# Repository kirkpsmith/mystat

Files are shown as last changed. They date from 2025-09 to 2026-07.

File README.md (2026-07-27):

# mystat

A USB-controlled potentiostat/galvanostat for electrochemistry measurements.

## Introduction
This repository contains all the necessary design files to build a USB-controlled potentiostat/galvanostat.  This repository is a modification of the original [tdstatv3](https://github.com/thomasdob/tdstatv3) designed by Thomas Dobbelaere and described in detail at https://arxiv.org/pdf/1701.07650.pdf.  The purpose of this fork is to make design changes that facilitate placing the instrument inside a protected enclosure suitable for an electrochemical research environment, including a wet chemical lab bench, fume hood, or glove box.

This version of the hardware design uses a PCB with dimensions of 55.5 mm by 70 mm to fit an EMI-shielded [extruded aluminum case](https://www.hammfg.com/files/parts/pdf/1457C801E.pdf) (IP 54 rated).  This board will also fit a similar watertight [extruded aluminum case](https://www.hammfg.com/files/parts/pdf/1457C801.pdf) (IP 65 rated).  The terminal block and surface mounted USB mini-B connector in the original tdstav3 design by Thomas Dobbelaere were replaced with IP 67 rated circular connectors for the USB and electrode cables.

In order to fit the case, tall components (such as the reed relays and crystal) had to be moved from the board edges that slide into the slots in the extruded aluminum.  As a result, the entire PCB layout was changed.  All traces were made as wide as possible given the PCB size constraints and component footprints.  In addition, this forked design eliminates the power and mode LEDs present in the original tdstatv3.  The choice to eliminate LEDs was made to avoid the need for creating holes in the case that would accommodate them.

## USB access on Linux
In order to access the device without requiring root privileges, create a file
`/etc/udev/rules.d/99-tdstatv3.rules` containing the line

```
SUBSYSTEM=="usb", ATTRS{idVendor}=="a0a0", ATTRS{idProduct}=="0002", GROUP="plugdev", MODE="0666"
```

If you are using an Arduino or similar to control pumps for flow battery experiments, you will need to make a similar file for that device, for example
`/etc/udev/rules.d/99-arduino.rules` and
```
SUBSYSTEM=="usb", ATTR{idVendor}=="1a86", ATTR{idProduct}=="7523", GROUP="plugdev", MODE="0666"
```

This assumes that the current user is a member of the `plugdev` group, and that the default USB Vendor and Product ID's
as coded in the microcontroller firmware are used; if not, these values need to be adjusted.

Reload of rules may be needed:
```
sudo udevadm control --reload
sudo udevadm trigger
```

## Windows Driver

To install the USB drivers in Windows, you must have Windows version 7 or later.  Download and run the program Zadig.exe found [here](https://github.com/pbatard/libwdi/releases/download/v1.5.1/zadig-2.9.exe).  The potentiostat should appear in the device list as "USB potentiostat/galvanostat".  Install the driver named "libusbK".

More information on Zadig can be found from its authors at: https://zadig.akeo.ie/

Zadig is based on libwdi and is licensed under GPLv3. The Zadig source code is found in the examples directory of the libwdi archive. The latest version of the source code may be downloaded from the git repository: https://github.com/pbatard/libwdi

## Credits
tdstatv3 created by:

* Thomas Dobbelaere
* email: thomas.dobbelaere@gmail.com

Previous fork created by:

* Matthew Yates
* email: myates@che.rochester.edu

Current fork created by:

* [Daniel Fernandez Pinto](https://chemisting.com) and [Kirk Smith](https://dualpower.supply)

## License
The contents of this repository are licensed under the GNU General Public License (GPL).

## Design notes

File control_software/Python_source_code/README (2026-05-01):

In this directory, create a virtual environment, activate it, and install the required packages:
```
python3 -m venv .venv
source .venv/bin/activate
python3 -m pip install -r requirements.txt
```

Run the program (sudo may be needed on Linux for USB privileges)
```
sudo .venv/bin/python mystat.py
```

On Linux, the following commands are sometimes needed:
```
export LD_LIBRARY_PATH=$(python3 -c "import PyQt5.QtCore; print(PyQt5.QtCore.QLibraryInfo.location(PyQt5.QtCore.QLibraryInfo.LibrariesPath))"):$LD_LIBRARY_PATH
export QT_QPA_PLATFORM_PLUGIN_PATH=$(python3 -c "import PyQt5.QtCore; print(PyQt5.QtCore.QLibraryInfo.location(PyQt5.QtCore.QLibraryInfo.PluginsPath))")

```

To package the app, download [appimagetool](https://github.com/AppImage/appimagetool/releases) to this directory, rename to `appimagetool`, and run
```
./build-appimage.sh
 ```

To update requirements.txt:

```
python -m pip freeze > requirements.txt
```

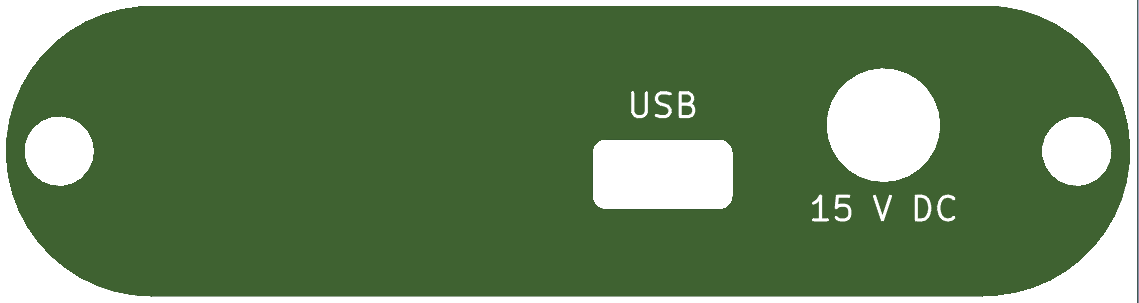
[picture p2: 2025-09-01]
hardware/backpanel/backpanel_image.png

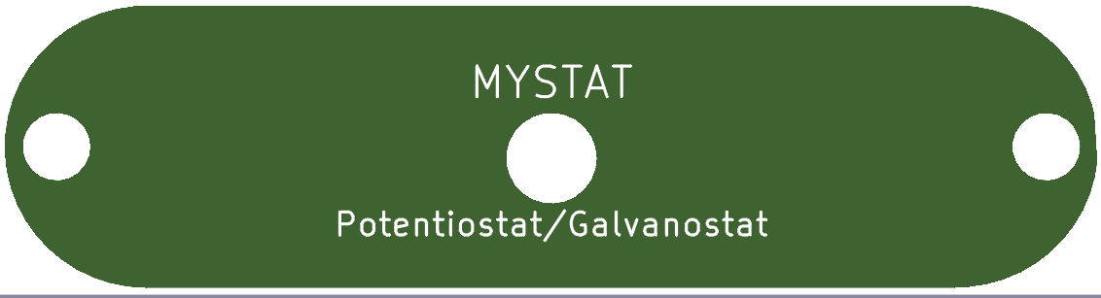
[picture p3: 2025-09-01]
hardware/frontpanel/frontpanel_image.png

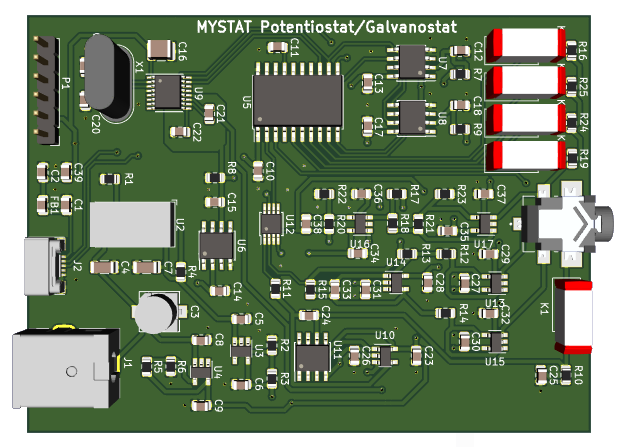
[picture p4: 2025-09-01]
hardware/mystat_circuit_board/circuit_board_image.png

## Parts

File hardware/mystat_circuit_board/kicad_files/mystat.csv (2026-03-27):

Value | Reference | Footprint | Qty | Part Number
10 nF | C1,C22 | Capacitor_SMD:C_0805_2012Metric | 2 | C0805C103J5GACTU
100 nF | C2,C10,C11,C12,C13,C14,C15,C17,C18,C23,C25,C26,C27,C28,C29,C30,C31,C32,C34,C35,C36,C37 | Capacitor_SMD:C_0805_2012Metric | 22 | 08055C104KAT2A
47 uF | C3 | my_footprints:EEE-FT1V470AR | 1 | EEE-FT1V470AR
4.7 uF | C4,C7 | Capacitor_SMD:C_1206_3216Metric | 2 | CL31B475KBHNNNE
4.7 uF | C5,C6,C8,C9,C39 | Capacitor_SMD:C_0805_2012Metric | 5 | C2012X7R1V475K125AC
10 uF | C16 | Capacitor_SMD:C_1210_3225Metric | 1 | CL32B106KBJNNWE
12 pF | C19,C20,C33,C38 | Capacitor_SMD:C_0805_2012Metric | 4 | CC0805JRNPO9BN120
3.3 nF | C21 | Capacitor_SMD:C_0805_2012Metric | 1 | GRM2165C1H332JA01D
4700 pF | C24 | Capacitor_SMD:C_0805_2012Metric | 1 | CC0805KRX7R9BB472
ILBB0805ER320V | FB1 | Capacitor_SMD:C_0805_2012Metric | 1 | ILBB0805ER320V
PJ-063AH | J1 | my_footprints:CUI_PJ-063AH | 1 | PJ-063AH
2173157-3 | J2 | my_footprints:CONN_2173157-3 | 1 | 2173157-3
SJ1-42534-SMT | J3 | my_footprints:CUI_SJ1-42534-SMT | 1 | SJ1-42534-SMT-TR
9011-05-11 | K1,K2,K3,K4,K5 | my_footprints:relay_9011-05-11 | 5 | 9011-05-11
ICSP | P1 | Connector_PinHeader_2.54mm:PinHeader_1x06_P2.54mm_Vertical | 1 | PRPC006SAAN-RC
60.4 kΩ | R1 | Resistor_SMD:R_0805_2012Metric | 1 | ERJ-6ENF6042V
8.87 kΩ* | R2 | Resistor_SMD:R_0805_2012Metric | 1 | ERA-6AEB8871V
88.7 kΩ* | R3 | Resistor_SMD:R_0805_2012Metric | 1 | ERJ-PB6B8872V
178 kΩ | R4 | Resistor_SMD:R_0805_2012Metric | 1 | ERJ-6ENF1783V
294 kΩ* | R5 | Resistor_SMD:R_0805_2012Metric | 1 | ERJ-PB6B2943V
174 kΩ* | R6 | Resistor_SMD:R_0805_2012Metric | 1 | ERJ-PB6B1743V
1k | R7,R9 | Resistor_SMD:R_0805_2012Metric | 2 | RC0805FR-071KL
10k | R8,R11 | Resistor_SMD:R_0805_2012Metric | 2 | RC0805FR-0710KL
27R | R10 | Resistor_SMD:R_0805_2012Metric | 1 | ERJ-6ENF27R0V
402k* | R12,R14 | Resistor_SMD:R_0805_2012Metric | 2 | ERA-6AEB4023V
75k* | R13,R15,R17,R18,R20,R22 | Resistor_SMD:R_0805_2012Metric | 6 | ERA-6AEB753V
100k* | R16 | Resistor_SMD:R_0805_2012Metric | 1 | ERA-6AEB104V
1k* | R19 | Resistor_SMD:R_0805_2012Metric | 1 | ERA-6AEB102V
18k* | R21 | Resistor_SMD:R_0805_2012Metric | 1 | ERA-6AEB183V
2k* | R23 | Resistor_SMD:R_0805_2012Metric | 1 | ERA-6AEB202V
10R* | R24 | Resistor_SMD:R_0805_2012Metric | 1 | 2-1625868-7
1R* | R25 | Resistor_SMD:R_0805_2012Metric | 1 | RL1220S-1R0-F
LTM8045 | U2 | my_footprints:BGA-40_6.25x11.25mm_Layout5x8_P1.25mm | 1 | LTM8045IY
ADP7182AUJZ-R7 | U3 | my_footprints:TSOT-23-5 | 1 | ADP7182AUJZ-R7
ADP7118AUJZ-5.0-R7 | U4 | my_footprints:TSOT-23-5 | 1 | ADP7118AUJZ-5.0-R7
PIC16F1459 | U5 | my_footprints:SOIC-20W | 1 | PIC16F1459-I/SO
ADR421 | U6 | my_footprints:SOIC-8 | 1 | ADR421ARZ
MCP3550-60 | U7,U8 | my_footprints:SOIC-8 | 2 | MCP3550-60E/SN
DAC1220 | U9 | my_footprints:DAC1220 | 1 | DAC1220E
OPA192 | U10,U13,U14,U15,U16,U17 | my_footprints:OPA192 | 6 | OPA192IDBVR
BUF634A | U11 | my_footprints:SOIC-8 | 1 | BUF634AIDR
ADG1419 | U12 | my_footprints:MSOP-8_3x3mm_P0.65mm | 1 | ADG1419BRMZ-REEL7
2.5 MHz | X1 | Crystal:Crystal_HC49-U_Vertical | 1 | ECS-25-S-1X

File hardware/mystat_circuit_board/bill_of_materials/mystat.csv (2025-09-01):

References | Manufacturer | Part Number | Value | Footprint | Quantity | Price(each) | Source
C1, C22 | KEMET | C0805C103J5GACTU | 10 nF | C_0805_2012Metric | 2 | 0.76 | Digikey ‎399-7992-1-ND‎
C16 | Samsung Electro-Mechanics | CL32B106KBJNNWE | 10 µF | C_1210_3225Metric | 1 | 0.66 | Digikey ‎1276-3388-1-ND‎
C19, C20, C33, C38 | Yageo | CC0805JRNPO9BN120 | 12 pF | C_0805_2012Metric | 4 | 0.11 | Digikey ‎311-1100-1-ND‎
C2, C10, C11, C12, C13, C14, C15, C17, C18, C23, C25, C26, C27, C28, C29, C30, C31, C32, C34, C35, C36, C37 | AVX Corporation | 08055C104KAT2A | 0.1 µF | C_0805_2012Metric | 22 | 0.15 | Digikey ‎478-1395-1-ND
C21 | Murata Electronics North America | GRM2165C1H332JA01D | 3.3 nF | C_0805_2012Metric | 1 | 0.25 | Digikey ‎490-1632-1-ND‎
C24 | Yageo | CC0805KRX7R9BB472 | 4700 pF | C_0805_2012Metric | 1 | 0.11 | Digikey ‎311-1133-1-ND‎
C3 | Panasonic Electronic Components | EEE-FT1V470AR | 47 μF | EEE-FT1V470AR | 1 | 0.5 | Digikey ‎PCE5014CT-ND‎
C4, C7 | Samsung Electro-Mechanics | CL31B475KBHNNNE | 4.7 μF | C_1206_3216Metric | 2 | 0.36 | Digikey ‎1276-2789-1-ND‎
C5, C6, C8, C9, C39 | TDK Corporation | C2012X7R1V475K125AC | 4.7 µF | C_0805_2012Metric | 5 | 0.73 | Digikey ‎445-7555-1-ND‎
FB1 | Vishay Dale | ILBB0805ER320V | Ferrite_Bead | C_0805_2012Metric | 1 | 0.1 | Digikey 541-2296-1-ND‎
J1 | CUI Inc. | PJ-063AH | PJ-063AH | CUI_PJ-063AH | 1 | 1.36 | ‎Digikey CP-063AH-ND‎
J2 | TE Connectivity AMP Connectors | 2173157-3 | 2173157-3 | CONN_2173157-3 | 1 | 3.39 | Digikey A124356CT-ND‎
J3 | CUI Inc. | SJ1-42534-SMT-TR | SJ1-42534-SMT | CUI_SJ1-42534-SMT | 1 | 1.2 | Digikey CP1-42534SJCT-ND
K1, K2, K3, K4, K5 | Coto Technology | 9011-05-11 | 9011-05-11 | relay_9011-05-11 | 5 | 7.97 | Digikey 306-1131-ND‎
P1 | Sullins Connector Solutions | PRPC006SAAN-RC | ICSP | PinHeader_1x06_P2.54mm_Vertical | 1 | 0.19 | Digikey S1011EC-06-ND‎
R1 | Panasonic Electronic Components | ERJ-6ENF6042V | 60.4 kΩ | R_0805_2012Metric | 1 | 0.1 | Digikey P60.4KCCT-ND‎
R10 | Panasonic Electronic Components | ERJ-6ENF27R0V | 27R | R_0805_2012Metric | 1 | 0.1 | Digikey P27.0CCT-ND‎
R12, R14 | Panasonic Electronic Components | ERA-6AEB4023V | 402k* | R_0805_2012Metric | 2 | 0.36 | Digikey P402KDACT-ND‎
R13, R15, R17, R18, R20, R22 | Panasonic Electronic Components | ERA-6AEB753V | 75k* | R_0805_2012Metric | 6 | 0.36 | Digikey P75KDACT-ND
R16 | Panasonic Electronic Components | ERA-6AEB104V | 100k* | R_0805_2012Metric | 1 | 0.36 | Digikey P100KDACT-ND
R19 | Panasonic Electronic Components | ERA-6AEB102V | 1k* | R_0805_2012Metric | 1 | 0.36 | Digikey P18KDACT-ND
R2 | Panasonic Electronic Components | ERA-6AEB8871V | 8.87 kΩ* | R_0805_2012Metric | 1 | 0.36 | Digikey P8.87KDACT-ND‎
R21 | Panasonic Electronic Components | ERA-6AEB183V | 18k* | R_0805_2012Metric | 1 | 0.36 | Digikey P18KDACT-ND
R23 | Panasonic Electronic Components | ERA-6AEB202V | 2k* | R_0805_2012Metric | 1 | 0.36 | Digikey P2.0KDACT-ND‎
R24 | TE Connectivity Passive Product | 2-1625868-7 | 10R* | R_0805_2012Metric | 1 | 0.53 | Digikey A110351CT-ND
R25 | Susumu | RL1220S-1R0-F | 1R* | R_0805_2012Metric | 1 | 0.33 | Digikey RL12S1.00FCT-ND
R3 | Panasonic Electronic Components | ERJ-PB6B8872V | 88.7 kΩ* | R_0805_2012Metric | 1 | 0.36 | Digikey P20816CT-ND
R4 | Panasonic Electronic Components | ERJ-6ENF1783V | 178 kΩ | R_0805_2012Metric | 1 | 0.1 | Digikey ‎P178KCCT-ND‎
R5 | Panasonic Electronic Components | ERJ-PB6B2943V | 294 kΩ* | R_0805_2012Metric | 1 | 0.36 | Digikey P20873CT-ND‎
R6 | Panasonic Electronic Components | ERJ-PB6B1743V | 174 kΩ* | R_0805_2012Metric | 1 | 0.36 | Digikey P20847CT-ND‎
R7, R9 | Yageo | RC0805FR-071KL | 1k | R_0805_2012Metric | 2 | 0.1 | Digikey 311-1.00KCRCT-ND
R8, R11 | Yageo | RC0805FR-0710KL | 10k | R_0805_2012Metric | 2 | 0.1 | Digikey 311-10.0KCRCT-ND‎
U10, U13, U14, U15, U16, U17 | Texas Instruments | OPA192IDBVR | OPA192 | OPA192 | 6 | 2.68 | Digikey 296-42105-1-ND‎
U11 | Texas Instruments | BUF634AIDR | BUF634A | SOIC-8 | 1 | 2.92 | Digikey 296-53619-1-ND‎
U12 | Analog Devices Inc. | ADG1419BRMZ-REEL7 | ADG1419 | MSOP-8_3x3mm_P0.65mm | 1 | 4.53 | Digikey ADG1419BRMZ-REEL7CT-ND‎
U2 | Linear Technology/Analog Devices | LTM8045IY | LTM8045 | BGA-40_6.25x11.25mm_Layout5x8_P1.25mm | 1 | 21.07 | Digikey LTM8045IY-ND‎
U3 | Analog Devices Inc. | ADP7182AUJZ-R7 | ADP7182AUJZ-R7 | TSOT-23-5 | 1 | 3.71 | Digikey ADP7182AUJZ-R7CT-ND‎
U4 | Analog Devices Inc. | ADP7118AUJZ-5.0-R7 | ADP7118AUJZ-5.0-R7 | TSOT-23-5 | 1 | 2.27 | Digikey ADP7118AUJZ-5.0-R7CT-ND
U5 | Microchip Technology | PIC16F1459-I/SO | PIC16F1459 | SOIC-20W | 1 | 1.77 | Digikey PIC16F1459-I/SO-ND‎
U6 | Analog Devices Inc. | ADR421ARZ | ADR421 | SOIC-8 | 1 | 6.81 | Digikey ‎ADR421ARZ-REEL7CT-ND
U7, U8 | Microchip Technology | MCP3550-60E/SN | MCP3550-60 | SOIC-8 | 2 | 3.98 | Digikey MCP3550-60E/SN-ND‎
U9 | Texas Instruments | DAC1220E | DAC1220 | DAC1220 | 1 | 19.8 | Digikey DAC1220E-ND‎
X1 | ECS Inc. | ECS-25-S-1X | 2.5 MHz | Crystal_HC49-U_Vertical | 1 | 1.13 | Digikey X1003-ND‎
E1 | Tensility International | 10-00340 | N.A. | N.A. | 1 | 4.44 | Digikey ‎839-1035-ND
E2 | Cinch Connectivity Solutions Johnson | 105-0302-001 | N.A. | N.A. | 1 | 1.14 | Digikey J103-ND
E3 | Cinch Connectivity Solutions Johnson | 105-0303-001 | N.A. | N.A. | 1 | 1.28 | Digikey J104-ND
E4 | Cinch Connectivity Solutions Johnson | 105-0304-001 | N.A. | N.A. | 1 | 1.17 | Digikey J301-ND
E5 | Cinch Connectivity Solutions Johnson | 105-0301-001 | N.A. | N.A. | 1 | 1.17 | Digikey J300-ND
E6-E9 | Cal Test Electronics | CT3759-0 | N.A. | N.A. | 4 | 2 | Digikey CT3759-0-ND
E10 | CUI Inc. | SDI30-15-U-P5 | N.A. | N.A. | 1 | 17.88 | Digikey 102-4106-ND
E11 | Hammond Manufacturing | 1455B802 | N.A. | N.A. | 1 | 9.6 | Digikey HM1117-ND
E12 | CUI Devices | AC-C13 NA | N.A. | N.A. | 1 | 3.76 | Digikey T1249-C13-NA-ND

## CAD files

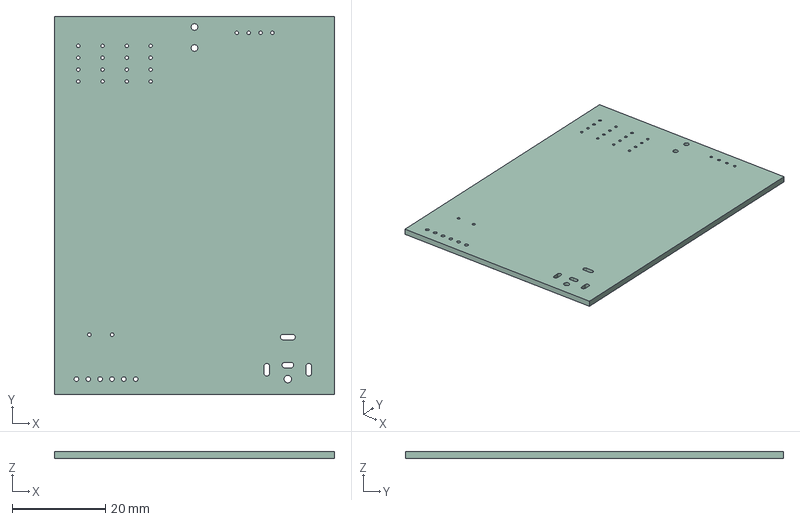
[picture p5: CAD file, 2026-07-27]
hardware/mystat_circuit_board/kicad_files/.step
60.0 x 81.0 x 1.51 mm

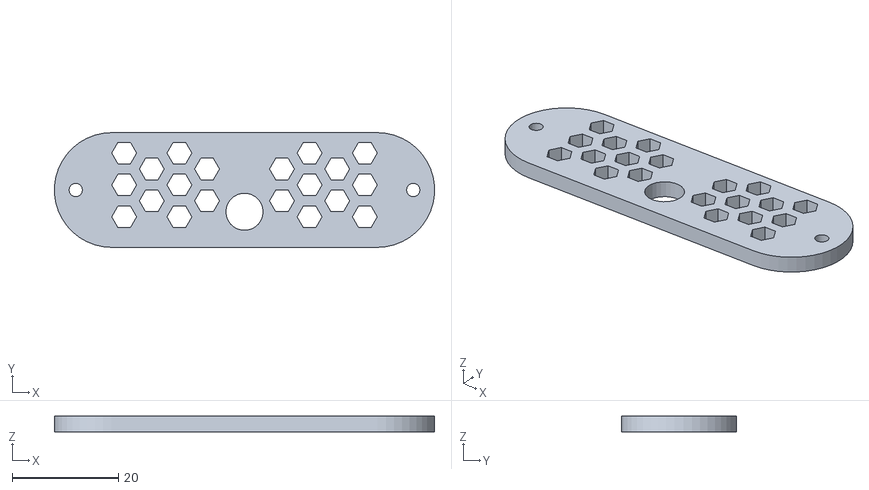
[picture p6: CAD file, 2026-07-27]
hardware/printable_case/Cable Panel.stl
71.5 x 21.6 x 3.00

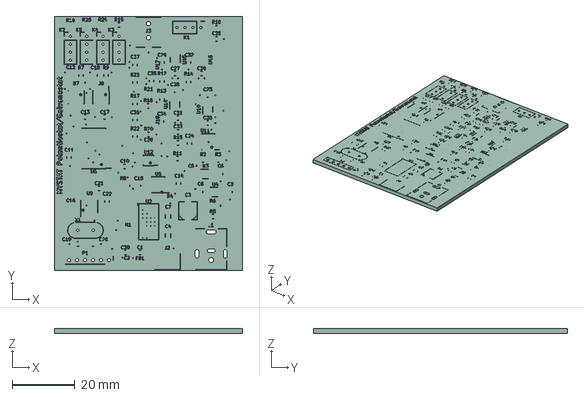
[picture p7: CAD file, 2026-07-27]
hardware/mystat_circuit_board/kicad_files/board.step
60.0 x 81.0 x 1.66 mm
mystat_silkscreen x 2
mystat_PCB

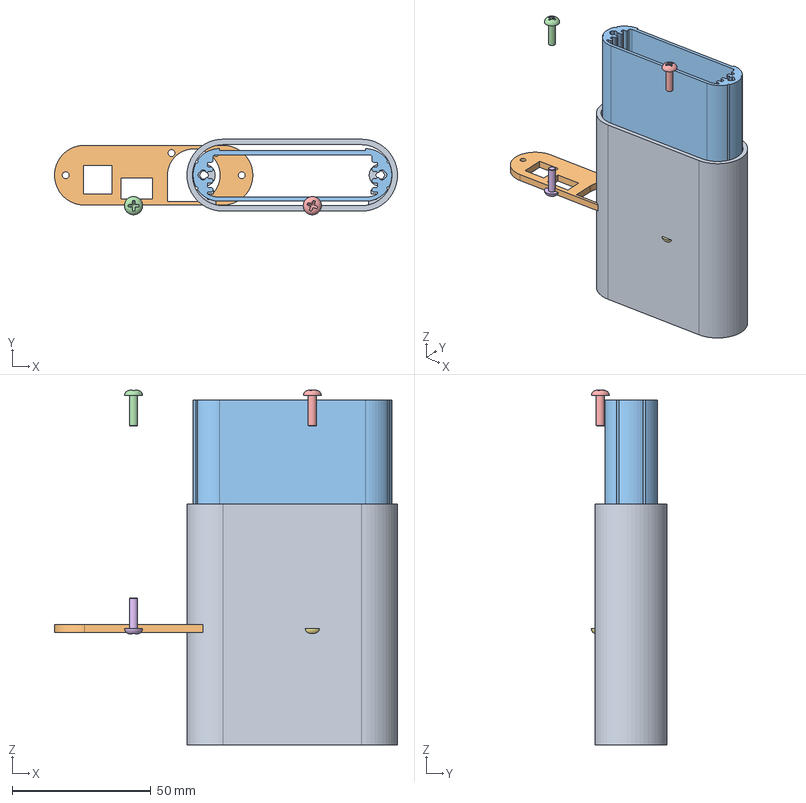
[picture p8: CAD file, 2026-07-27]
hardware/printable_case/case.FCStd
123.8 x 27.3 x 128.0 mm
Fan-USB-Power Panel
1455B80
6-32 screw-flange
6-32 screw-flange001
6-32 screw-flange002
6-32 screw-flange003

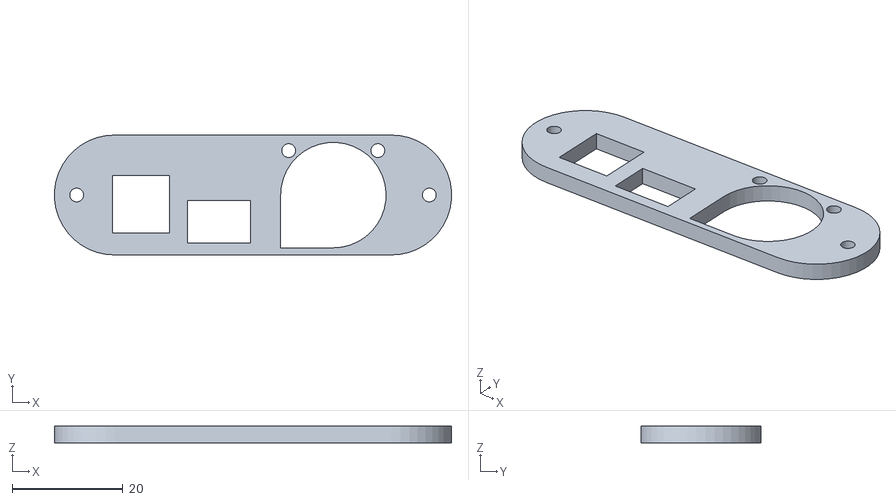
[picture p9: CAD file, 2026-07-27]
hardware/printable_case/Fan-USB-Power Panel.stl
71.5 x 21.6 x 3.00

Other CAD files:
hardware/printable_case/Case.stl

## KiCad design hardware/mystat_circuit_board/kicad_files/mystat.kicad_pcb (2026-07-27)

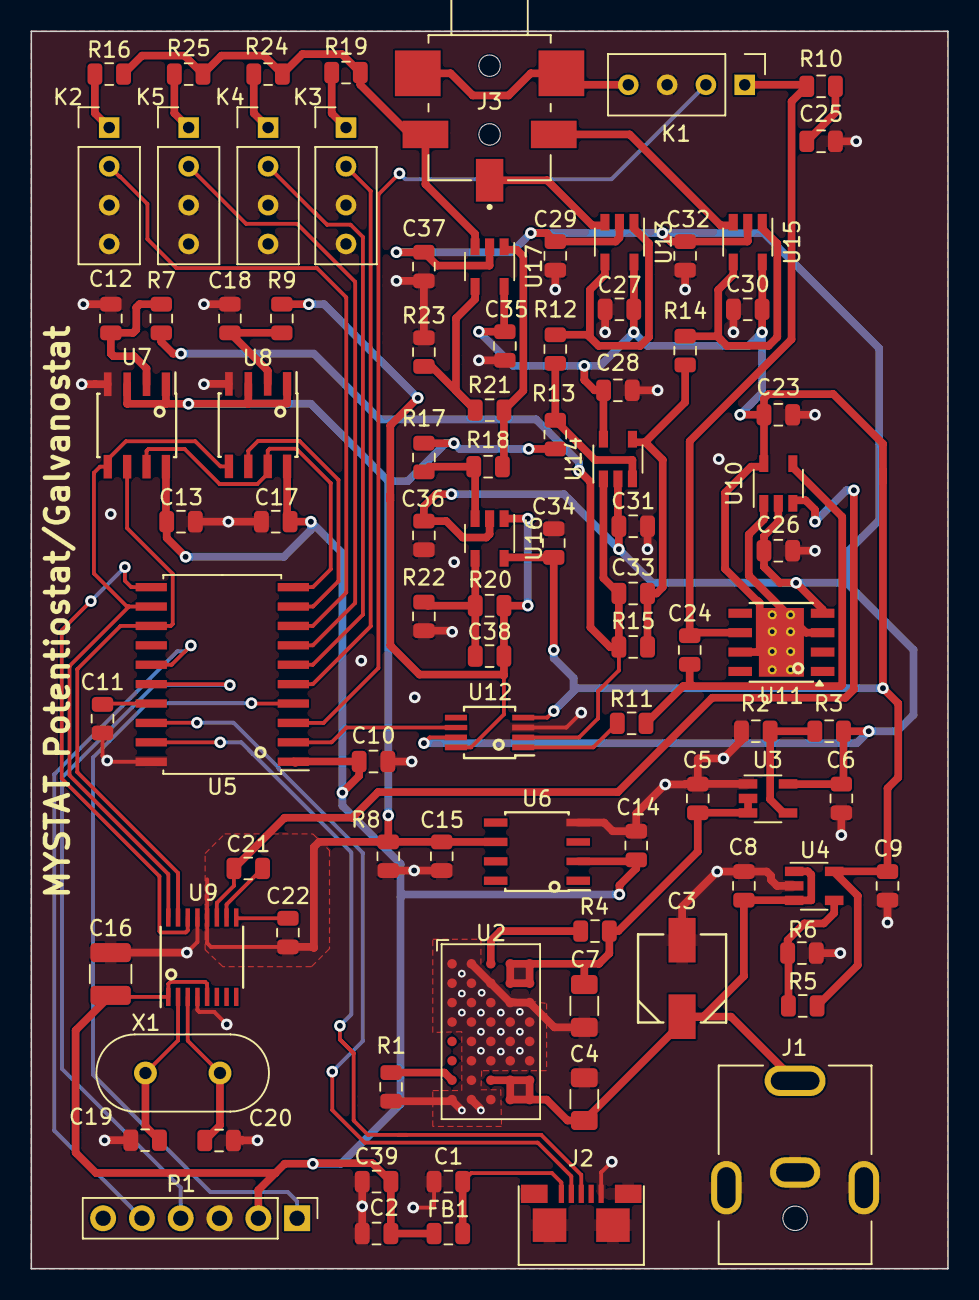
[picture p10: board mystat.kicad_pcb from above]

Board: 4 copper layers, 60.0 x 81.0 mm, 91 parts (0 on the bottom side), 59 nets.

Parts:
C1, C22: 10 nF; C_0805_2012Metric
C2, C10, C11, C12, C13, C14, C15, C17, C18, C23, C25, C26, C27, C28, C29, C30, C31, C32, C34, C35, C36, C37: 100 nF; C_0805_2012Metric
C3: 47 uF; EEE-FT1V470AR
C4, C7: 4.7 uF; C_1206_3216Metric
C5, C6, C8, C9, C39: 4.7 uF; C_0805_2012Metric
C16: 10 uF; C_1210_3225Metric
C19, C20, C33, C38: 12 pF; C_0805_2012Metric
C21: 3.3 nF; C_0805_2012Metric
C24: 4700 pF; C_0805_2012Metric
FB1: 32 Ω; C_0805_2012Metric
J1: PJ-063AH; CUI_PJ-063AH
J2: 2173157-3; CONN_2173157-3
J3: SJ1-42534-SMT; CUI_SJ1-42534-SMT
K1, K2, K3, K4, K5: 9011-05-11; relay_9011-05-11
P1: ICSP; PinHeader_1x06_P2.54mm_Vertical
R1: 60.4 kΩ; R_0805_2012Metric
R2: 8.87 kΩ*; R_0805_2012Metric
R3: 88.7 kΩ*; R_0805_2012Metric
R4: 178 kΩ; R_0805_2012Metric
R5: 294 kΩ*; R_0805_2012Metric
R6: 174 kΩ*; R_0805_2012Metric
R7, R9: 1k; R_0805_2012Metric
R8, R11: 10k; R_0805_2012Metric
R10: 27R; R_0805_2012Metric
R12, R14: 402k*; R_0805_2012Metric
R13, R15, R17, R18, R20, R22: 75k*; R_0805_2012Metric
R16: 100k*; R_0805_2012Metric
R19: 1k*; R_0805_2012Metric
R21: 18k*; R_0805_2012Metric
R23: 2k*; R_0805_2012Metric
R24: 10R*; R_0805_2012Metric
R25: 1R*; R_0805_2012Metric
U2: LTM8045; BGA-40_6.25x11.25mm_Layout5x8_P1.25mm
U3: ADP7182AUJZ-R7; TSOT-23-5
U4: ADP7118AUJZ-5.0-R7; TSOT-23-5
U5: PIC16F1459; SOIC-20W
U6: ADR421; SOIC-8
U7, U8: MCP3550-60; SOIC-8
U9: DAC1220
U10, U13, U14, U15, U16, U17: OPA192
U11: BUF634AIDDAR; TI_SO-PowerPAD-8_ThermalVias
U12: ADG1419; MSOP-8_3x3mm_P0.65mm
X1: 2.5 MHz; Crystal_HC49-U_Vertical

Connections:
+5V: C2.2, C10.1, C13.1, C14.1, C16.1, C17.1, C39.2, FB1.2, P1.2, U5.1 (VDD), U6.2 (VIN), U7.8 (VDD), U8.8 (VDD), U9.1 (DVDD), U9.5 (AVDD)
+13.4V: C9.2, C23.2, C27.2, C28.1, C30.2, C34.1, C35.2, R5.1, U4.5 (VOUT), U10.5 (V+), U11.7 (V+), U12.4 (V+), U13.5 (V+), U14.5 (V+), U15.5 (V+), U16.5 (V+), U17.5 (V+)
+15V: C3.1, C4.1, C8.2, J1.1, U2.G3 (PIN_G3), U2.G4 (PIN_G4), U2.G5 (PIN_G5), U2.H4 (PIN_H4), U2.H5 (PIN_H5), U4.1 (VIN), U4.3 (EN)
-13.4V: C6.2, C26.1, C29.2, C31.1, C32.2, C36.1, C37.1, R3.2, U3.5 (VOUT), U10.2 (V-), U11.4 (V-), U11.9 (THPAD), U12.7 (V-), U13.2 (V-), U14.2 (V-), U15.2 (V-), U16.2 (V-), U17.2 (V-)
-15V: C5.2, C7.1, R4.2, U2.A4 (PIN_A4), U2.A5 (PIN_A5), U2.B4 (PIN_B4), U2.B5 (PIN_B5), U3.2 (VIN), U3.3 (EN)
CE: J3.2, R16.1, R19.1, R24.1, R25.1, U17.3 (+)
CELL_ON: K1.2, U5.3 (RA4)
CS1: U5.11 (RB6), U9.14 (CS)
CS2: U5.10 (RB7), U7.7 (CS), U8.7 (CS)
DAC_out: C21.2, U9.11 (VOUT), U10.3 (+)
GND: C1.1, C2.1, C3.2, C4.2, C5.1, C6.1, C7.2, C8.1, C9.1, C10.2, C11.2, C12.2, C13.2, C14.2, C15.2, C16.2, C17.2, C18.2, C19.2, C20.2, C23.1, C25.2, C26.2, C27.1, C28.2, C29.1, C30.1, C31.2, C32.1, C34.2, C35.1, C36.2, C37.2, C39.1, J1.2, J1.3 (SHIELD), J2.5, J2.S1 (SHIELD), J2.S2 (SHIELD), J2.S3 (SHIELD), J2.S4 (SHIELD), K1.3, K2.3, K2.4, K3.3, K3.4, K4.3, K4.4, K5.3, K5.4, P1.3, R1.2, R2.1, R6.2, R8.2, R22.2, R23.2, U2.A1 (PIN_A1), U2.A2 (PIN_A2), U2.B1 (PIN_B1), U2.B2 (PIN_B2), U2.B3 (PIN_B3), U2.C1 (PIN_C1), U2.C2 (PIN_C2), U2.C3 (PIN_C3), U2.C4 (PIN_C4), U2.C5 (PIN_C5), U2.D1 (PIN_D1), U2.D2 (PIN_D2), U2.D3 (PIN_D3), U2.D4 (PIN_D4), U2.D5 (PIN_D5), U2.E2 (PIN_E2), U2.E3 (PIN_E3), U2.E4 (PIN_E4), U2.E5 (PIN_E5), U2.F2 (PIN_F2), U2.F3 (PIN_F3), U2.F4 (PIN_F4), U2.F5 (PIN_F5), U2.G2 (PIN_G2), U2.H1 (PIN_H1), U2.H2 (PIN_H2), U2.H3 (PIN_H3), U3.1 (GND), U4.2 (GND), U5.20 (VSS), U6.4 (GND), U7.4 (VSS), U8.4 (VSS), U9.4 (DGND), U9.13 (AGND), U12.3 (GND)
I_MEAS: C38.2, R9.1, R20.2, U12.8 (SB), U16.1
MODE_SW: U5.2 (RA5), U12.6 (IN)
unnamed: C1.2, FB1.1, J2.1
unnamed: C24.1, K1.1, R10.1, U11.6
unnamed: C25.1, R10.2
unnamed: K2.1, R16.2
unnamed: K3.1, R19.2
unnamed: K4.1, R24.2
unnamed: K5.1, R25.2
unnamed: P1.1, U5.4 (/MCLR)
unnamed: P1.4, U5.16 (RC0)
unnamed: P1.5, U5.15 (RC1)
unnamed: R4.1, U2.A3 (PIN_A3)
unnamed: R1.1, U2.G1 (PIN_G1)
unnamed: R2.2, R3.1, U3.4 (ADJ)
unnamed: R5.2, R6.1, U4.4 (SE/ADJ)
unnamed: J2.3, U5.19 (D+)
unnamed: J2.2, U5.18 (D-)
unnamed: C11.1, U5.17 (VUSB)
unnamed: C12.1, R7.2, U7.2 (VIN+)
unnamed: C18.1, R9.2, U8.2 (VIN+)
unnamed: C22.1, U9.9 (C1)
unnamed: C21.1, U9.10 (C2)
unnamed: C20.1, U9.3 (XIN), X1.2
unnamed: C19.1, U9.2 (XOUT), X1.1
unnamed: C24.2, R11.1, U10.4 (-)
unnamed: U10.1, U11.3 (V_{IN})
unnamed: R11.2, U12.1 (D)
unnamed: R12.2, U13.1, U13.4 (-)
unnamed: R12.1, R13.1, U14.3 (+)
unnamed: C33.1, R14.1, R15.2, U14.4 (-)
unnamed: R14.2, U15.1, U15.4 (-)
unnamed: R17.2, R18.2, U16.3 (+)
unnamed: C38.1, R20.1, R22.1, U16.4 (-)
unnamed: R21.1, R23.1, U17.4 (-)
unnamed: R18.1, R21.2, U17.1
RANGE1: K5.2, U5.7 (RC3)
RANGE2: K4.2, U5.6 (RC4)
RANGE3: K3.2, U5.5 (RC5)
RANGE4: K2.2, U5.8 (RC6)
RE: J3.3, U15.3 (+)
SCK: U5.12 (RB5), U7.5 (SCK), U8.5 (SCK), U9.16 (SCLK)
SDIO: U5.13 (RB4), U7.6 (SDO), U9.15 (SDIO)
SDIO2: U5.9 (RC7), U8.6 (SDO)
SE: J3.1, U13.3 (+)
V_MEAS: C33.2, R7.1, R15.1, U12.2 (SA), U14.1
Vref: C15.1, C22.2, R8.1, R13.2, R17.1, U6.6 (VOUT), U7.1 (VREF), U7.3 (VIN-), U8.1 (VREF), U8.3 (VIN-), U9.12 (VREF)
WE: J3.4, K1.4

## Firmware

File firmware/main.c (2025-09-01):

/*
 * USB Potentiostat/galvanostat firmware
 *
 * This code makes use of Signal 11's M-Stack USB stack to implement 
 * communication through raw USB bulk transfers. Commands are received
 * as ASCII strings on EP1 OUT. They are then interpreted and executed;
 * they either change the state of output pins, or cause data to be read
 * from / written to the MCP3550 (ADC) or DAC1220 (DAC) using a software
 * SPI implementation. The resulting data, or an "OK" message, is sent as
 * a reply on EP1 IN. The USB service is interrupt-driven.
 *
 * Thomas Dobbelaere
 * CoCooN research group
 * 2016-06-07
 */

#include "usb.h"
#include <xc.h>
#include <string.h>
#include "usb_config.h"
#include "usb_ch9.h"
#include "spi_software.h"
#include "Flash.h"
#include "HEFlash.h"

// PIC16F1459 configuration bit settings:
// CONFIG1
#pragma config FOSC = INTOSC    // Oscillator Selection Bits (INTOSC oscillator: I/O function on CLKIN pin)
#pragma config WDTE = OFF       // Watchdog Timer Enable (WDT disabled)
#pragma config PWRTE = OFF      // Power-up Timer Enable (PWRT disabled)
#pragma config MCLRE = OFF      // MCLR Pin Function Select (MCLR/VPP pin function is digital input)
#pragma config CP = OFF         // Flash Program Memory Code Protection (Program memory code protection is disabled)
#pragma config BOREN = ON       // Brown-out Reset Enable (Brown-out Reset enabled)
#pragma config CLKOUTEN = OFF   // Clock Out Enable (CLKOUT function is disabled. I/O or oscillator function on the CLKOUT pin)
#pragma config IESO = OFF       // Internal/External Switchover Mode (Internal/External Switchover Mode is disabled)
#pragma config FCMEN = OFF      // Fail-Safe Clock Monitor Enable (Fail-Safe Clock Monitor is disabled)

// CONFIG2
#pragma config WRT = OFF        // Flash Memory Self-Write Protection (Write protection off)
#pragma config CPUDIV = NOCLKDIV// CPU System Clock Selection Bit (NO CPU system divide)
#pragma config USBLSCLK = 48MHz // USB Low Speed Clock Selection bit (System clock expects 48 MHz, FS/LS USB CLKENs divide-by is set to 8.)
#pragma config PLLMULT = 3x     // PLL Multipler Selection Bit (3x Output Frequency Selected)
#pragma config PLLEN = ENABLED  // PLL Enable Bit (3x or 4x PLL Enabled)
#pragma config STVREN = ON      // Stack Overflow/Underflow Reset Enable (Stack Overflow or Underflow will cause a Reset)
#pragma config BORV = LO        // Brown-out Reset Voltage Selection (Brown-out Reset Voltage (Vbor), low trip point selected.)
#pragma config LPBOR = OFF      // Low-Power Brown Out Reset (Low-Power BOR is disabled)
#pragma config LVP = ON        // Low-Voltage Programming Enable (High-voltage on MCLR/VPP must be used for programming)

#define _XTAL_FREQ 48000000     // 48 MHz CPU clock frequency

#define MODE_SW_PIN LATAbits.LATA5
#define MODE_SW_TRIS TRISAbits.TRISA5
#define CELL_ON_PIN LATAbits.LATA4
#define CELL_ON_TRIS TRISAbits.TRISA4
#define CELL_ON  1
#define CELL_OFF 0
#define POTENTIOSTATIC  0
#define GALVANOSTATIC  1
#define INPUT  1
#define OUTPUT 0
#define RANGE1_PIN LATCbits.LATC3
#define RANGE1_TRIS TRISCbits.TRISC3
#define RANGE2_PIN LATCbits.LATC4
#define RANGE2_TRIS TRISCbits.TRISC4
#define RANGE3_PIN LATCbits.LATC5
#define RANGE3_TRIS TRISCbits.TRISC5
#define RANGE4_PIN LATCbits.LATC6
#define RANGE4_TRIS TRISCbits.TRISC6

static const uint8_t* received_data;
static uint8_t received_data_length;
static uint8_t* transmit_data;
static uint8_t transmit_data_length;
static uint8_t heflashbuffer[FLASH_ROWSIZE];

void InitializeIO()
{
	OSCCONbits.IRCF = 0b1111; // 0b1111 = 16MHz HFINTOSC postscaler
	ANSELA = 0x00; // digital I/O on PORTA
	ANSELB = 0x00; // digital I/O on PORTB
	ANSELC = 0x00; // digital I/O on PORTC
	APFCON = 0x00; // no funny alternate pins
	MODE_SW_TRIS = OUTPUT;
	MODE_SW_PIN = POTENTIOSTATIC; // initialize mode to potentiostatic
	CELL_ON_TRIS = OUTPUT;
	CELL_ON_PIN = CELL_OFF; // initialize cell to off position
	RANGE1_TRIS = OUTPUT;
	RANGE2_TRIS = OUTPUT;
	RANGE3_TRIS = OUTPUT;
	RANGE4_TRIS = OUTPUT;
	RANGE1_PIN = 1; // initialize range to range 1
	RANGE2_PIN = 0;
	RANGE3_PIN = 0;
	RANGE4_PIN = 0;
	InitializeSPI();
	__delay_ms(25); // power-up delay - necessary for DAC1220
	DAC1220_Reset();
	__delay_ms(25);
	DAC1220_Init();
	HEFLASH_readBlock(heflashbuffer, 2, FLASH_ROWSIZE); // get dac calibration
	DAC1220_Write3Bytes(8, heflashbuffer[0], heflashbuffer[1], heflashbuffer[2]); // apply dac calibration
	DAC1220_Write3Bytes(12, heflashbuffer[3], heflashbuffer[4], heflashbuffer[5]); 
}

void command_unknown()
{
	const uint8_t* reply = "?";
    strcpy(transmit_data, reply);
    transmit_data_length = strlen(reply);
}

void send_OK()
{
	const uint8_t* reply = "OK";
    strcpy(transmit_data, reply);
    transmit_data_length = strlen(reply);
}

void command_cell_on()
{
	CELL_ON_PIN = CELL_ON;
	send_OK();
}

void command_cell_off()
{
	CELL_ON_PIN = CELL_OFF;
	send_OK();
}

void command_mode_potentiostatic()
{
	MODE_SW_PIN = POTENTIOSTATIC;
	send_OK();
}

void command_mode_galvanostatic()
{
	MODE_SW_PIN = GALVANOSTATIC;
	send_OK();
}

void command_range1()
{
    RANGE1_PIN = 1;
    __delay_ms(10); // make the new relay setting before breaking the old one
    RANGE2_PIN = 0;
    RANGE3_PIN = 0;
    RANGE4_PIN = 0;
	send_OK();
}

void command_range2()
{
    RANGE2_PIN = 1;
    __delay_ms(10); // make the new relay setting before breaking the old one
    RANGE1_PIN = 0;
    RANGE3_PIN = 0;
    RANGE4_PIN = 0;
	send_OK();
}

void command_range3()
{
    RANGE3_PIN = 1;
    __delay_ms(10); // make the new relay setting before breaking the old one
    RANGE1_PIN = 0;
    RANGE2_PIN = 0;
    RANGE4_PIN = 0;
	send_OK();
}

void command_range4()
{
    RANGE4_PIN = 1;
    __delay_ms(10); // make the new relay setting before breaking the old one
    RANGE1_PIN = 0;
    RANGE2_PIN = 0;
    RANGE3_PIN = 0;
	send_OK();
}

void command_set_dac(const uint8_t* dac_data)
{
	DAC1220_Write3Bytes(0, dac_data[0], dac_data[1], dac_data[2]);
	send_OK();
}

void command_calibrate_dac()
{
	DAC1220_SelfCal();
	__delay_ms(500); // wait until calibration is finished
	uint8_t data[6];
	DAC1220_Read3Bytes(8, data, data+1, data+2); // get calibration data
	DAC1220_Read3Bytes(12, data+3, data+4, data+5);
	HEFLASH_writeBlock(2, data, 6); // save calibration data to HEFLASH
	send_OK();
}

void command_read_adc()
{
	uint8_t adc_data[6];
	if(MCP3550_Read(adc_data))
	{
		transmit_data_length=6;
		memcpy(transmit_data, adc_data, transmit_data_length);
	}
	else
	{
		const uint8_t* reply = "WAIT";
		strcpy(transmit_data, reply);
		transmit_data_length = strlen(reply);
	}
}

void command_read_offset()
{
	HEFLASH_readBlock(heflashbuffer, 1, FLASH_ROWSIZE);
	transmit_data_length=6;
	memcpy(transmit_data, heflashbuffer, transmit_data_length);
}

void command_save_offset(const uint8_t* offset_data)
{
	HEFLASH_writeBlock(1, offset_data, 6);
	send_OK();
}

void command_read_shuntcalibration()
{
	HEFLASH_readBlock(heflashbuffer, 3, FLASH_ROWSIZE);
	transmit_data_length=8;
	memcpy(transmit_data, heflashbuffer, transmit_data_length);
}

void command_save_shuntcalibration(const uint8_t* shuntcalibration_data)
{
	HEFLASH_writeBlock(3, shuntcalibration_data, 8);
	send_OK();
}

void command_read_dac_cal()
{
	HEFLASH_readBlock(heflashbuffer, 2, FLASH_ROWSIZE);
	transmit_data_length=6;
	memcpy(transmit_data, heflashbuffer, transmit_data_length);
}

void command_set_dac_cal(const uint8_t* dac_cal_data)
{
	HEFLASH_writeBlock(2, dac_cal_data, 6);
	DAC1220_Write3Bytes(8, dac_cal_data[0], dac_cal_data[1], dac_cal_data[2]);
	DAC1220_Write3Bytes(12, dac_cal_data[3], dac_cal_data[4], dac_cal_data[5]);
	send_OK();
}

void interpret_command() {
    if (received_data_length == 7 && strncmp(received_data,"CELL ON",7) == 0)
        command_cell_on();
    else if (received_data_length == 8 && strncmp(received_data,"CELL OFF",8) == 0)
        command_cell_off();
    else if (received_data_length == 14 && strncmp(received_data,"POTENTIOSTATIC",14) == 0)
        command_mode_potentiostatic();
    else if (received_data_length == 13 && strncmp(received_data,"GALVANOSTATIC",13) == 0)
        command_mode_galvanostatic();
    else if (received_data_length == 7 && strncmp(received_data,"RANGE 1",7) == 0)
        command_range1();
    else if (received_data_length == 7 && strncmp(received_data,"RANGE 2",7) == 0)
        command_range2();
    else if (received_data_length == 7 && strncmp(received_data,"RANGE 3",7) == 0)
        command_range3();
    else if (received_data_length == 7 && strncmp(received_data,"RANGE 4",7) == 0)
        command_range4();
    else if (received_data_length == 10 && strncmp(received_data,"DACSET ",7) == 0)
	command_set_dac(received_data+7);
    else if (received_data_length == 6 && strncmp(received_data,"DACCAL",6) == 0)
	command_calibrate_dac();
    else if (received_data_length == 7 && strncmp(received_data,"ADCREAD",7) == 0)
	command_read_adc();
    else if (received_data_length == 10 && strncmp(received_data,"OFFSETREAD",10) == 0)
	command_read_offset();
    else if (received_data_length == 17 && strncmp(received_data,"OFFSETSAVE ",11) == 0)
	command_save_offset(received_data+11);
    else if (received_data_length == 9 && strncmp(received_data,"DACCALGET",9) == 0)
	command_read_dac_cal();
    else if (received_data_length == 16 && strncmp(received_data,"DACCALSET ",10) == 0)
	command_set_dac_cal(received_data+10);
    else if (received_data_length == 12 && strncmp(received_data,"SHUNTCALREAD",12) == 0)
	command_read_shuntcalibration();
    else if (received_data_length == 21 && strncmp(received_data,"SHUNTCALSAVE ",13) == 0)
	command_save_shuntcalibration(received_data+13);
    else
        command_unknown();
}

int main(void)
{
	InitializeIO();

	// Enable Active clock-tuning from the USB
	ACTCONbits.ACTSRC = 1; // 1=USB
	ACTCONbits.ACTEN = 1;

	// Configure interrupts
	INTCONbits.PEIE = 1;
	INTCONbits.GIE = 1;

	// Initialize USB
	usb_init();

	while (1)
	{
		if (usb_is_configured() && usb_out_endpoint_has_data(1)) // wait for data received from host
		{
			if (!usb_in_endpoint_halted(1))
			{
				while (usb_in_endpoint_busy(1)) // wait for EP1 IN to become free
					;
				received_data_length = usb_get_out_buffer(1, &received_data); // get memory location and length of received data
				transmit_data = usb_get_in_buffer(1); // get memory location of data to transmit
				interpret_command(); // this reads received_data and sets transmit_data and transmit_data_length
				usb_send_in_buffer(1, transmit_data_length); // send the data back
			}
			usb_arm_out_endpoint(1);
		}
	}

	return 0;
}

void interrupt isr()
{
	usb_service();
}

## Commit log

2018-07-02 Update parts_list.txt
    Removed indicator LEDs.
2018-07-02 Update parts_list.txt
    Replaced terminal block with shielded 4-position circular connector.
2018-07-02 Update parts_list.txt
    Replaced SMD usb port with 5 pin receptacle for mating with a Bulgin panel mounted USB cable.
2018-07-02 Delete pcb_3dview.png
    Does not illustrate modified design.
2018-07-02 Add files via upload
    3D rendering of modified PCB design.
2018-07-02 Delete pcb_fabrication_diagram.pdf
    Does not represent modified PCB design.
2018-07-02 Add files via upload
    Shows modified board layout.
2018-07-02 Add files via upload
    Modified schematic to remove indicator LEDs.
2018-07-02 Delete tdstatv3-B.Cu.gbl
    Does not represent modified design.
    [tdstatv3-B.Cu.gbl]
2018-07-02 Add files via upload
    Showing modified PCB design.
    [mystatv1-B.Cu.gbl]
2018-07-02 Delete tdstatv3-B.Mask.gbs
    Does not represent modified PCB layout.
    [tdstatv3-B.Mask.gbs]
2018-07-02 Delete tdstatv3-Edge.Cuts.gm1
    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
    [tdstatv3-Edge.Cuts.gm1]
2018-07-02 Delete tdstatv3-F.Cu.gtl
    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
    [tdstatv3-F.Cu.gtl]
2018-07-02 Delete tdstatv3-F.Mask.gts
    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
    [tdstatv3-F.Mask.gts]
2018-07-02 Delete tdstatv3-F.SilkS.gto
    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
    [tdstatv3-F.SilkS.gto]
2018-07-02 Delete tdstatv3-NPTH.drl
    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
    [tdstatv3-NPTH.drl]
2018-07-02 Delete tdstatv3.drl
    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
    [tdstatv3.drl]
2018-07-02 Add files via upload
    Modified PCB layout/design.
    [mystatv1-B.Mask.gbs, mystatv1-Edge.Cuts.gm1, mystatv1-F.Cu.gtl, mystatv1-F.Mask.gts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]
2018-07-02 Delete pcb_3dview
    File name was missing PNG extension.
2018-07-02 Add files via upload
    3D rendering of modified PCB layout/design.
2018-07-02 Delete led_3mm_red.wings
    Not used in modified design.
2018-07-02 Delete led_3mm_red.wrl
    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
2018-07-02 Delete DUO-LED-3mm.kicad_mod
    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
2018-07-02 Delete fp-lib-table
    Does not represent modified PCB layout/design.
2018-07-02 Delete mylib.bck
    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
2018-07-02 Delete mylib.dcm
    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
2018-07-02 Delete mylib.lib
    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
2018-07-02 Delete tdstatv3
    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
2018-07-02 Delete tdstatv3-cache.lib
    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
2018-07-02 Delete tdstatv3.bak
    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
2018-07-02 Delete tdstatv3.csv
    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
    [tdstatv3.csv]
2018-07-02 Delete tdstatv3.kicad_pcb
    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
    [tdstatv3.kicad_pcb]
2018-07-02 Delete tdstatv3.kicad_pcb-bak
    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
2018-07-02 Delete tdstatv3.net
    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
2018-07-02 Delete tdstatv3.pro
    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
2018-07-02 Delete tdstatv3.sch
    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
    [tdstatv3.sch]
2018-07-02 Delete tdstatv3.xml
    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
2018-07-02 Add files via upload
    Kicad files for modified PCB layout/design
    [mystatv1.csv, mystatv1.kicad_pcb, mystatv1.sch]
2018-07-14 Update README.md
    New PCB dimensions and new case selected.
2018-07-14 Add files via upload
    Changed layout. Added guard ring for the DAC1220. Used wider traces. Manually routed everything.
    [mystatv1.kicad_pcb]
2018-07-16 Add files via upload
    Added symbol for the USB terminal with Pin 1 labeled for power input.
2018-07-16 Add files via upload
    Name changed. Created using Kicad version 5. Added datasheets, manufacturer, and manufacturer part number for all components. This schematic passes the electrical rules check in Kicad.
    [mystat.sch]
2018-07-16 Add files via upload
    Named changed. PCB dimensions changed to 80mm x 80mm. Used wider traces throughout. Added guard ring for U6 following Texas Instruments datasheet guidelines. Reorganized components to minimize length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
    [mystat.kicad_pcb]
2018-07-16 Add files via upload
    Bill of materials created using KiBOM_CLI plugin in Kicad version 5. Added manufacturer and part numbers to facilitate creating a shopping cart at Digi-Key or other supplier.
    [mystat_bom_1.csv]
2018-07-16 Add files via upload
    Used unpolarized capacitor symbols through since the ceramic capacitors are all non-polarized.
2018-07-16 Add files via upload
    Showing new PCB layout.
2018-07-17 Add files via upload
    Revised layout.
    [mystat-NPTH.drl]
2018-07-17 Delete mystat-Edge.Cuts.gbr
    Changed to Protel file extensions.
    [mystat-Edge.Cuts.gbr]
2018-07-17 Add files via upload
    Revised layout using Protel file extensions.
    [mystat-Edge.Cuts.gm1]
2018-07-17 Delete mystatv1-Edge.Cuts.gm1
    Replaced with revised layout.
    [mystatv1-Edge.Cuts.gm1]
2018-07-17 Delete mystatv1-B.Mask.gbs
    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
    [mystatv1-B.Mask.gbs]
2018-07-17 Delete mystatv1-F.Mask.gts
    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
    [mystatv1-F.Mask.gts]
2018-07-17 Delete mystatv1-F.SilkS.gto
    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
    [mystatv1-F.SilkS.gto]
2018-07-17 Delete mystatv1-F.Paste.gtp
    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
    [mystatv1-F.Paste.gtp]
2018-07-17 Delete mystatv1-B.Cu.gbl
    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
    [mystatv1-B.Cu.gbl]
2018-07-17 Delete mystatv1-F.Cu.gtl
    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
    [mystatv1-F.Cu.gtl]
2018-07-26 Add files via upload
    Picture of board with latest revision of PCB layout.
2018-07-26 Update README.md
    Edited to explain design choices made in latest PCB layout.
2018-07-26 Delete pcb_fabrication_diagram.pdf
    Replaced with new fabrication diagram in PNG image format.
2018-07-26 Add files via upload
    Shows latest PCB layout.
2018-07-26 Add files via upload
    Modified PCB layout.
2018-07-26 Add files via upload
    Changed title and date with modified PCB layout.
    [mystat.sch]
2018-07-26 Add files via upload
    Modified PCB layout. Made overall PCB dimensions smaller to fit the chosen case, all traces were made as wide as possible, changed relative position of all components in an attempt to minimize overal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
    [mystat.kicad_pcb]
2018-07-26 Add files via upload
    Used with latest PCB layout.
2018-07-26 Add files via upload
    Fixed error in footprint. The largest mechanical holes were moved slightly close together. This should allow the plastic clips on this component to attach to the PCB.
2018-07-26 Add files via upload
    Revised PCB layout.
    [mystat.drl]
2018-07-26 Delete mystat-PTH.drl
    Combined PTH and NPTH into one drl file with revised layout.
    [mystat-PTH.drl]
2018-07-26 Delete mystat-NPTH.drl
    Combined PTH and NPTH into one drl file with revised PCB layout.
    [mystat-NPTH.drl]
2018-07-26 Update README.md
    Corrected PCB width dimension.
2018-07-27 Add files via upload
    Changed title and date.
    [mystat.sch]
2018-07-27 Add files via upload
    Corrected PCB trace routing to provide more direct ground return paths.
    [mystat.kicad_pcb]
2018-07-27 Delete mystat-B.SilkS.gbo
    Not using silk screen on back side of board.
    [mystat-B.SilkS.gbo]
2018-07-27 Delete mystat-B.Paste.gbp
    No SMD parts on back side of board.
    [mystat-B.Paste.gbp]
2018-07-27 Add files via upload
    New layout of traces for better ground return paths.
    [mystat.drl]
2018-07-27 Delete mystat_bom_1.csv
    New BOM will be uploaded to main project page.
    [mystat_bom_1.csv]
2018-07-27 Add files via upload
    Modified to include 3D image of M12 circular connector for electrode cables.
2018-07-27 Add files via upload
    3D image of circular connector created from manufacturer supplied *.stp file.
2018-07-27 Add files via upload
    Footprint updated for circular connector.
    [mystat.kicad_pcb]
2018-07-27 Add files via upload
    Bill of materials created using KiBOM plugin.
    [bom.csv]
2018-07-27 Update README.md
    Added description of bill of materials csv file.
2018-07-27 Add files via upload
    Parts list from Digiket shopping cart.
    [partslist.csv]
2018-07-27 Add files via upload
    Updated part numbers with what is presently in stock at Digikey.
    [mystat.sch]
2018-07-27 Add files via upload
    Updated with parts presently in stock at Digikey.
    [bom.csv]
2024-04-07 Daniel added functionality to connect to Arduino for pump speed control
2024-04-27 Daniel fixed serial connections to motor control arduino, refresh serial ports and simultaneous motor speed control
2024-05-20 added files for printable case that Josh Hauser designed
    [MyStat Back Panel v15.stl, MyStat Front Panel 2.5 v7.stl, MyStat Housing Body 2.0 v13.stl]
2024-07-03 arduino pump control now only updates pump speed when slider is released, not continuously as slider moves to new values
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2025-09-01 Upload 3d-printable case designed by Josh Hauser and firmware folder from https://doi.org/10.5281/zenodo.3979793
    [MyStat Back Panel v15.stl, MyStat Front Panel 2.5 v7.stl, MyStat Housing Back Panel.stl, MyStat Housing Body 2.0 v13.stl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]
2025-09-01 moved things around to match as closely as possible the Zenodo upload from Yates
    [MyStat Housing Back Panel.stl, MyStat Housing Body.stl, MyStat Housing Front Panel.stl, analog.sch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]
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2026-03-27 update to KiCAD 10
    [analog.kicad_sch, digital.kicad_sch, mystat-NPTH.drl, mystat-PTH.drl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]
2026-05-01 merged Daniel's changes in to GUI. getting things ready in KiCAD 10 and finding substitute parts
    [analog.kicad_sch, analog.sch, digital.kicad_sch, digital.sch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]
2026-05-01 revert to KiCAD 10 state before attempting reed relay changes, to merge into master
    [analog.kicad_sch, analog.sch, digital.kicad_sch, digital.sch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]

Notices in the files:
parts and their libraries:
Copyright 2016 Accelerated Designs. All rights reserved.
